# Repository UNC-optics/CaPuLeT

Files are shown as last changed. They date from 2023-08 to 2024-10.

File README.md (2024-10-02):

# An open-source system to integrate Calcium-imaging, Pupillometry, and Locomotion-estimated Tracking (CaPuLeT) in head-fixed mice

Designed by members of the [Pégard](https://www.nicolaspegard.com/) and [Rodríguez-Romaguera](https://www.rodriguezromagueralab.org/) Labs at the University of North Carolina at Chapel Hill, **CaPuLeT** allows researchers to capture locomotion, pupil dynamics, and body kinematics simultaneously. Our system relies on CMOS cameras, an infrared camera placed at eye-level to capture pupil size and an additional camera to record body kinematics. Our system is capable of capturing  locomotion, or the mouse's movement across time, as our wheel system is attached to a mounted rotary encoder. For more information, refer to [Ortiz-Juza et al, 2024](https://star-protocols.cell.com/protocols/3752) [1].



# Graphic User Interface (GUI)

The **CaPuLeT** MATLAB graphical user interface (GUI) allows users to trigger and manage the cameras and LEDs driven by an Arduino microcontroller with a custom shield. Within **CaPuLeT**, users can track locomotion, pupil-size, and *in vivo* calcium imaging data in real-time. 

**Behavioral and Imaging Data Collected**:
- IR Camera → Pupil Dynamics (Dilation and Constriction)
- Additional Camera → Body Kinematics (Body and Tail Movement)
- Rotary Encoder → Locomotion (Speed and Acceleration)
- Multi-Photon Microscope → Neuronal Activity (Intracellular Calcium Concentration)

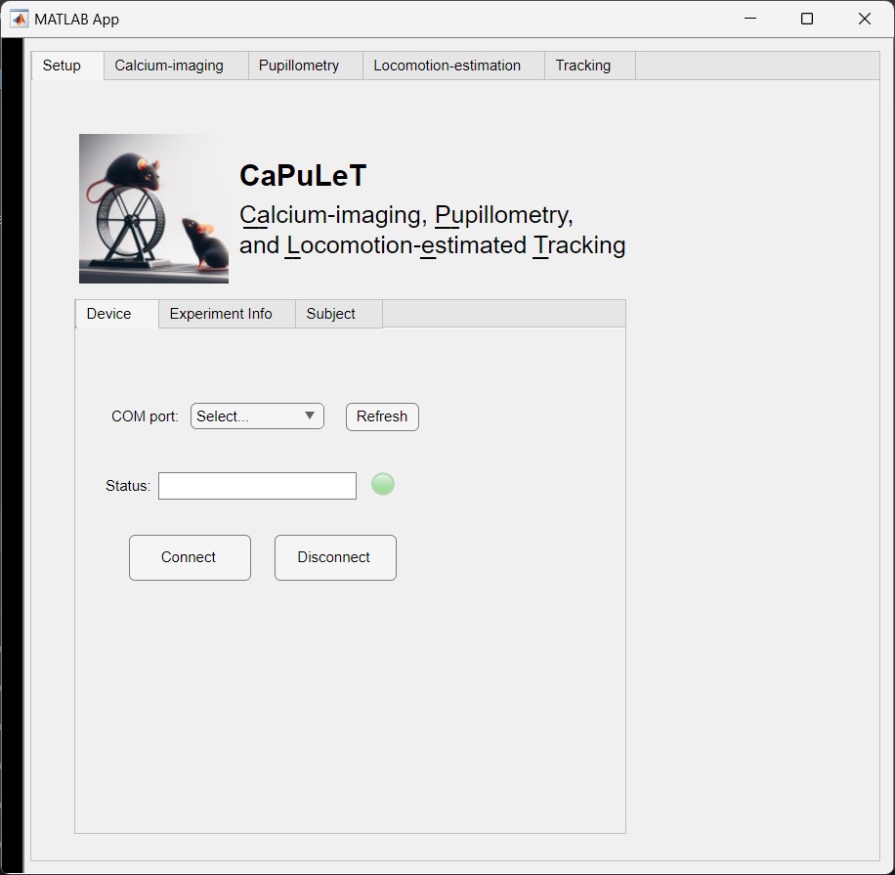
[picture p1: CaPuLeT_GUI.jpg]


# Custom Arduino Printed Circuit Board Shield:
The head-fixation wheel system is driven and controlled by an Arduino Mega 2560 microcontroller board, with a custom printed circuit board (PCB) Arduino shield with built-in resistance, interactive feedback LEDs, real-time clock compatibility, and screw hole terminals. The printed circuit board shield expands the capabilities of the microcontroller board and allows for greater stability than a conventional solderless circuit board. The Arduino shield allows users to interface with each of the components of the **CaPuLeT** GUI. 

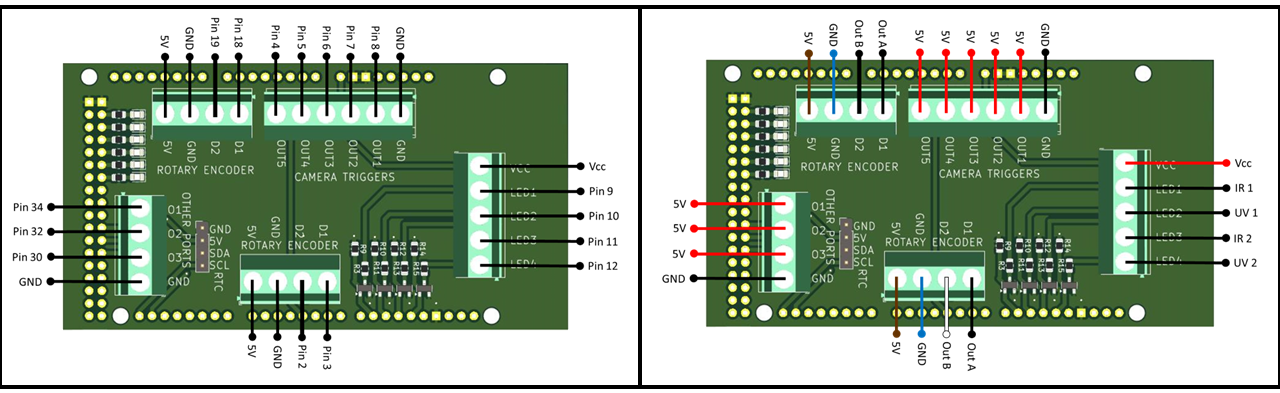
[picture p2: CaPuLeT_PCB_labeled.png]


# Commercially Available and Custom Made Parts 

The following [component list](https://github.com/UNC-optics/CaPuLeT/blob/b9dc13ef048e2fede86db514f3f39af26186ab3a/1-CaPuLeT-Components-Table.pdf) details the manufacturer, part number, and quantity of each item required. This [version](https://github.com/UNC-optics/CaPuLeT/blob/b9dc13ef048e2fede86db514f3f39af26186ab3a/2-CaPuLeT-Color-Coded-Components-Table.pdf) of the component list contains a color coded key which provides an additional layer of support when building the system. 

<table class="table table-bordered table-hover table-condensed">
<thead><tr><th title="Field #1">Part Number</th>
<th title="Field #2">Distributor</th>
<th title="Field #3">Part Name</th>
<th title="Field #4">Distributor Part Number</th>
<th title="Field #5">Quantity Needed</th>
<th title="Field #6">Unit Price</th>
<th title="Field #7">Total Price</th>
</tr></thead>
<tbody><tr>
<td align="right">1</td>
<td>McMaster</td>
<td>5 mm Linear Motion Shaft</td>
<td>6112K37</td>
<td>1</td>
<td>$10.98 </td>
<td>$10.98 </td>
</tr>
<tr>
<td align="right">2</td>
<td>McMaster</td>
<td>Clear Impact-Resistant Polycarbonate Film</td>
<td>85585K15</td>
<td>1</td>
<td>$8.35 </td>
<td>$8.35 </td>
</tr>
<tr>
<td align="right">3</td>
<td>McMaster</td>
<td>Female Threaded Round Standoff</td>
<td>93330A541</td>
<td>10</td>
<td>$2.13 </td>
<td>$21.30 </td>
</tr>
<tr>
<td align="right">4</td>
<td>McMaster</td>
<td>Socket Head Screw M3 x 0.5 mm Thread, 6 mm Long</td>
<td>91290A111</td>
<td>1 (Pack of 100)</td>
<td>$10.91 </td>
<td>$10.91 </td>
</tr>
<tr>
<td align="right">5</td>
<td>Polulu</td>
<td>Aluminum Mounting Hub for 5mm Shaft</td>
<td>1203</td>
<td>1 (Pack of 2)</td>
<td>$18.90 </td>
<td>$18.90 </td>
</tr>
<tr>
<td align="right">6</td>
<td>Polulu</td>
<td>Machine Screw: #4-40, 1/2? Length, Phillips</td>
<td>1962</td>
<td>1 (Pack of 25)</td>
<td>$1.39 </td>
<td>$1.39 </td>
</tr>
<tr>
<td align="right">7</td>
<td>Thorlabs</td>
<td>0.75 Inch Post</td>
<td>TR075</td>
<td>1</td>
<td>$5.38 </td>
<td>$5.38 </td>
</tr>
<tr>
<td align="right">8</td>
<td>Thorlabs</td>
<td>2 Inch Post</td>
<td>TR2</td>
<td>2</td>
<td>$5.90 </td>
<td>$11.80 </td>
</tr>
<tr>
<td align="right">9</td>
<td>Thorlabs</td>
<td>3 Inch Post</td>
<td>TR3</td>
<td>2</td>
<td>$6.15 </td>
<td>$12.30 </td>
</tr>
<tr>
<td align="right">10</td>
<td>Thorlabs</td>
<td>4 Inch Post, 5 Pack</td>
<td>TR4-P5</td>
<td>1 (Pack of 5)</td>
<td>$30.00 </td>
<td>$30.00 </td>
</tr>
<tr>
<td align="right">11</td>
<td>Thorlabs</td>
<td>6 Inch Post</td>
<td>TR6</td>
<td>2</td>
<td>$8.09 </td>
<td>$16.18 </td>
</tr>
<tr>
<td align="right">12</td>
<td>Thorlabs</td>
<td>8 Inch Post</td>
<td>TR8</td>
<td>2</td>
<td>$9.69 </td>
<td>$19.38 </td>
</tr>
<tr>
<td align="right">13</td>
<td>Thorlabs</td>
<td>10 Inch Post</td>
<td>TR10</td>
<td>2</td>
<td>$10.76 </td>
<td>$21.52 </td>
</tr>
<tr>
<td align="right">14</td>
<td>Thorlabs</td>
<td>2 Inch Post Holder</td>
<td>PH2</td>
<td>1</td>
<td>$8.95 </td>
<td>$8.95 </td>
</tr>
<tr>
<td align="right">15</td>
<td>Thorlabs</td>
<td>3 Inch Post Holder</td>
<td>PH3</td>
<td>4</td>
<td>$9.62 </td>
<td>$38.48 </td>
</tr>
<tr>
<td align="right">16</td>
<td>Thorlabs</td>
<td>6 Inch Post Holder</td>
<td>PH6</td>
<td>1</td>
<td>$14.70 </td>
<td>$14.70 </td>
</tr>
<tr>
<td align="right">17</td>
<td>Thorlabs</td>
<td>Right Angle End Clamp</td>
<td>RA180</td>
<td>4</td>
<td>$12.34 </td>
<td>$49.36 </td>
</tr>
<tr>
<td align="right">18</td>
<td>Thorlabs</td>
<td>Rotating Clamp</td>
<td>SWC</td>
<td>1</td>
<td>$26.91 </td>
<td>$26.91 </td>
</tr>
<tr>
<td align="right">19</td>
<td>Thorlabs</td>
<td>Right Angle Post Clamp</td>
<td>RA90TR</td>
<td>1</td>
<td>$17.82 </td>
<td>$17.82 </td>
</tr>
<tr>
<td align="right">20</td>
<td>Thorlabs</td>
<td>Mini Optical Post</td>
<td>MS3R</td>
<td>1</td>
<td>$9.09 </td>
<td>$9.09 </td>
</tr>
<tr>
<td align="right">21</td>
<td>Thorlabs</td>
<td>Aluminum Breadboard 8&quot; x 10&quot; x 1/2&quot;, 1/4&quot;-20 Taps</td>
<td>MB810</td>
<td>1</td>
<td>$131.60 </td>
<td>$131.60 </td>
</tr>
<tr>
<td align="right">22</td>
<td>Thorlabs</td>
<td>Aluminum Breadboard 12&quot; x 18&quot; x 1/2&quot;, 1/4&quot;-20 Taps</td>
<td>MB1218</td>
<td>1</td>
<td>$214.65 </td>
<td>$214.65 </td>
</tr>
<tr>
<td align="right">23</td>
<td>Thorlabs</td>
<td>Breadboard Lifting Handles, Reinforced Polymer </td>
<td>BBH1</td>
<td>2 (Pack of 2)</td>
<td>$17.01 </td>
<td>$17.01 </td>
</tr>
<tr>
<td align="right">24</td>
<td>Thorlabs</td>
<td>4-40 Stainless Steel Cap Screw, 3/8&quot; Long</td>
<td>SH4S038</td>
<td>1 (Pack of 50)</td>
<td>$9.31 </td>
<td>$9.31 </td>
</tr>
<tr>
<td align="right">25</td>
<td>Thorlabs</td>
<td>Spring-Loaded 3/16&quot; Hex-Locking Thumbscrew, 1/4&quot;-20 Thread</td>
<td>TS25H</td>
<td>2</td>
<td>$2.87 </td>
<td>$5.74 </td>
</tr>
<tr>
<td align="right">26</td>
<td>Thorlabs</td>
<td>1/4&quot;-20 Stainless Steel Setscrew, 5/8&quot; Long (Adaptor)</td>
<td>SS25S0625</td>
<td>1 (Pack of 25)</td>
<td>$6.97 </td>
<td>$6.97 </td>
</tr>
<tr>
<td align="right">27</td>
<td>Thorlabs</td>
<td>1/4&quot; Washer, M6 Compatible, Stainless Steel</td>
<td>W25S050</td>
<td>1 (Pack of 100)</td>
<td>$10.20 </td>
<td>$10.20 </td>
</tr>
<tr>
<td align="right">28</td>
<td>Thorlabs</td>
<td>1/4&quot;-20 Stainless Steel Nut</td>
<td>N25S0440</td>
<td>1 (Pack of 50)</td>
<td>$6.43 </td>
<td>$6.43 </td>
</tr>
<tr>
<td align="right">29</td>
<td>Omron</td>
<td>Rotary Encoder - 1024 P/R (Quadrature)</td>
<td>E6B2-CWZ3E (E69-C06B)</td>
<td>1</td>
<td>$48.50 </td>
<td>$48.50 </td>
</tr>
<tr>
<td align="right">30</td>
<td>DB Unlimited</td>
<td>Speaker 80hm 5 w top port 104db</td>
<td>2104-SP500208-3-ND</td>
<td>1</td>
<td>$6.79 </td>
<td>$6.79 </td>
</tr>
<tr>
<td align="right">31</td>
<td>SullinsCorp</td>
<td>2.54mm Pitch Single Row Pin Header Strip</td>
<td>PREC040SAAN-RC</td>
<td>3</td>
<td>$1.53</td>
<td>$1.53</td>
</tr>
<tr>
<td align="right">32</td>
<td>Ardest</td>
<td>2N2222 NPN TO-92 Power Transistors</td>
<td>2N2222</td>
<td>6</td>
<td>$1.44</td>
<td>$1.44</td>
</tr>
<tr>
<td align="right">33</td>
<td>Boca Bearings</td>
<td>5 mm Steel Ball Bearing</td>
<td>SMR115-ZZC #5 LD</td>
<td>2</td>
<td>$10.58 </td>
<td>$21.16 </td>
</tr>
<tr>
<td align="right">34</td>
<td>Xenocam</td>
<td>9-22mm 1/3" F1.4 M12-mount lens with IR filter</td>
<td>XC0922LENS</td>
<td>1</td>
<td>$19.99 </td>
<td>$19.99 </td>
</tr>
<tr>
<td align="right">35</td>
<td>Monoprice</td>
<td>USB 2.0 Type-A Male to Mini-B 5pin Male Cable (Monoprice)</td>
<td>B002KL8J8W</td>
<td>1</td>
<td>$4.78</td>
<td>$4.78</td>
</tr>
<tr>
<td align="right">36</td>
<td>Computar</td>
<td>0.33-Inch Varifocal lens 2.8-12mm F1.3 Auto Iris (Computar)</td>
<td>B002HRE2ZS / TG4Z2813FCS-IR</td>
<td>1(Used)</td>
<td>$19.99 </td>
<td>$19.99 </td>
</tr>
<tr>
<td align="right">37</td>
<td>Chanzon</td>
<td>3 mm UV light, 395-400nm (Chanzon)</td>
<td>100F3T-YT-WH-PU</td>
<td>1 (Pack of 100)</td>
<td>$6.99 </td>
<td>$6.99 </td>
</tr>
<tr>
<td align="right">38</td>
<td>Adafruit</td>
<td>5 mm super-bright IR LED, 940nm (Adafruit)</td>
<td>ADA388 / B00ULB0U44</td>
<td>1 (Pack of 25)</td>
<td>$10.98 </td>
<td>$10.98 </td>
</tr>
<tr>
<td align="right">39</td>
<td>Fermerry</td>
<td>24 AWG 50 feet Electrical Wire (Fermerry)</td>
<td>B089CX3FVV</td>
<td>1</td>
<td>$26.99 </td>
<td>$26.99 </td>
</tr>
<tr>
<td align="right">40</td>
<td>Arduino</td>
<td>Arduino Mega 2560 Rev3 Microcontroller Board (Arduino)</td>
<td>A000067 / B0046AMGW0</td>
<td>1</td>
<td>$48.99 </td>
<td>$48.99 </td>
</tr>
<tr>
<td align="right">41</td>
<td>Arduino</td>
<td>USB 2.0 Cable Type A/B (Arduino)</td>
<td>M000006 / B013EOQUAW</td>
<td>1</td>
<td>$7.00 </td>
<td>$7.00 </td>
</tr>
<tr>
<td align="right">42</td>
<td>Tnisesm</td>
<td>PCB Mount Screw Terminal Block Connectors (Tnisesm)</td>
<td>CATN-T03B</td>
<td>1</td>
<td>$8.99 </td>
<td>$8.99 </td>
</tr>
<tr>
<td align="right">43</td>
<td>Adeep</td>
<td>Real Time Clock Module DS3231 AT24C32 IIC (Adeept)</td>
<td>2pcsDS3231 / B097PMNMQZ</td>
<td>1 (Pack of 2)</td>
<td>$7.99 </td>
<td>$7.99 </td>
</tr>
<tr>
<td align="right">44</td>
<td>LiCB</td>
<td>3V Lithium Battery (Junpower)</td>
<td>CR2032 / B07LGL9LQ1</td>
<td>1 (Pack of 10)</td>
<td>$4.99 </td>
<td>$4.99 </td>
</tr>
<tr>
<td align="right">45</td>
<td>ELECFUN</td>
<td>Heat Shrink Tubing (Electfun)</td>
<td>RSG-KIT350</td>
<td>1</td>
<td>$14.99 </td>
<td>$14.99 </td>
</tr>
<tr>
<td align="right">46</td>
<td>Yancorp</td>
<td>Black Adhesive contact paper (Yancorp)</td>
<td>B082CPSVPW</td>
<td>1</td>
<td>$6.98 </td>
<td>$6.98 </td>
</tr>
<tr>
<td align="right">47</td>
<td>Weld-On</td>
<td>IPS Weld-On 3 Acrylic Plastic Cement (Weld-On)</td>
<td>?TLLPN-21847771</td>
<td>1</td>
<td>$28.55 </td>
<td>$28.55 </td>
</tr>
<tr>
<td align="right">48</td>
<td>CENTROPOWER</td>
<td>12V 5A DC Power Cable Male Female Connector (Centro Power)</td>
<td>DCCORD-MF</td>
<td>1 (Pack of 10)</td>
<td>$9.19 </td>
<td>$9.19 </td>
</tr>
<tr>
<td align="right">49</td>
<td>CENTROPOWER</td>
<td>12V DC Power Connector Barrel Adaptor (Centro Power)</td>
<td>B07C61434H</td>
<td>1 (Pack of 10)</td>
<td>$7.99 </td>
<td>$7.99 </td>
</tr>
<tr>
<td align="right">50</td>
<td>ALITOVE</td>
<td>12V Red LED Flexible Strip Ribbon Light (Alitrove, 16.4 feet)</td>
<td>AL5RWPBK12V</td>
<td>1</td>
<td>$13.99 </td>
<td>$13.99 </td>
</tr>
<tr>
<td align="right">51</td>
<td>Mifasopower</td>
<td>Power Strip Surge Protector 10Ft (Mifaso Power)</td>
<td>MFS311T</td>
<td>1</td>
<td>$19.99 </td>
<td>$19.99 </td>
</tr>
<tr>
<td align="right">52</td>
<td>Sumato Stuff</td>
<td>Anti Vibration Pads (Functional Necessities)</td>
<td>SSHI00003</td>
<td>1 (Pack of 4)</td>
<td>$14.99 </td>
<td>$14.99 </td>
</tr>
<tr>
<td align="right">53</td>
<td>Focusound</td>
<td>1&quot; x 12&quot; x 12&quot; Sound Absorption Wall Panels (Xin &amp; Log)</td>
<td>FS0302A</td>
<td>1 (Pack of 24)</td>
<td>$17.99 </td>
<td>$17.99 </td>
</tr>
<tr>
<td align="right">54</td>
<td>TANTTI</td>
<td>4 inch Zip Ties with 18 lb Tensile Strength</td>
<td>604477847283</td>
<td>1 (Pack of 200)</td>
<td>$3.99 </td>
<td>$3.99 </td>
</tr>
<tr>
<td align="right">55</td>
<td>3M</td>
<td>3M Scotch Super 33+ Electrical Tape - 3/4 in x 52 ft</td>
<td>MMM06133</td>
<td>1</td>
<td>$4.98 </td>
<td>$4.98 </td>
</tr>
<tr>
<td align="right">56</td>
<td>Amazon</td>
<td>Hirose 4 Pin Female HR10A-7P-4S to Flying Leads Power Cable (Alvin’s Cables)</td>
<td>HR10A-7P-4S(73)</td>
<td>1</td>
<td>$25.99 </td>
<td>$25.99</td>
</tr>
<tr>
<td align="right">57</td>
<td>Custom Machined Parts</td>
<td>Rotary Encoder Adaptor (Aluminum 304)</td>
<td>CNC Machining (eMachineShop)</td>
<td>6 (Bulk Purchase)</td>
<td>$28.43 </td>
<td>$170.62 </td>
</tr>
<tr>
<td align="right">58</td>
<td>Custom Machined Parts</td>
<td>Head Plate Holder (Aluminum 304)</td>
<td>CNC Machining (eMachineShop)</td>
<td>12 (Bulk Purchase)</td>
<td>$30.20 </td>
<td>$362.44 </td>
</tr>
<tr>
<td align="right">59</td>
<td>Custom Machined Parts</td>
<td>Head Plate (Top Piece) (Aluminum 304)</td>
<td>CNC Machining (eMachineShop)</td>
<td>6 (Bulk Purchase)</td>
<td>$39.14 </td>
<td>$234.85 </td>
</tr>
<tr>
<td align="right">60</td>
<td>Custom Machined Parts</td>
<td>Head Plate (Bottom Piece) (Aluminum 304)</td>
<td>CNC Machining (eMachineShop)</td>
<td>6 (Bulk Purchase)</td>
<td>$51.01 </td>
<td>$306.04 </td>
</tr>
<tr>
<td align="right">61</td>
<td>Custom Machined Parts</td>
<td>Head rings (Aluminum 6061-T6)</td>
<td>CNC Machining (eMachineShop)</td>
<td>100 (Bulk Purchase)</td>
<td>$5.16 </td>
<td>$258.22 </td>
</tr>
<tr>
<td align="right">62</td>
<td>Custom Machined Parts</td>
<td>Rotary Wheel (1/8 Thick Clear Cast Acrylic)</td>
<td>Laser Cutting (Ponoko)</td>
<td>2</td>
<td>$61.06 </td>
<td>$61.06 </td>
</tr>
<tr>
<td align="right">63</td>
<td>Custom Machined Parts</td>
<td>Rotary Wheel Curved Surface (Clear Cast Acrylic)</td>
<td>Laser Cutting / Manual Cutting</td>
<td>1</td>
<td>$0.00 </td>
<td>$0.00 </td>
</tr>
<tr>
<td align="right">64</td>
<td>Custom Machined Parts</td>
<td>Rotary Wheel Curved Surface (Black Adhesive Contact Paper)</td>
<td>Laser Cutting / Manual Cutting</td>
<td>1</td>
<td>$0.00 </td>
<td>$0.00 </td>
</tr>
<tr>
<td align="right">65</td>
<td>Custom Machined Parts</td>
<td>Waste Management Ramp (Resin)</td>
<td>3-D Printing (Craftcloud3d)</td>
<td>1</td>
<td>$57.76 </td>
<td>$57.76 </td>
</tr>
<tr>
<td align="right">66</td>
<td>Custom Machined Parts</td>
<td>Arduino Mega 2560 Rev3 Protective Case (Resin)</td>
<td>3-D Printing (Craftcloud3d)</td>
<td>1</td>
<td>$16.06 </td>
<td>$16.06 </td>
</tr>
<tr>
<td align="right">67</td>
<td>Custom Machined Parts</td>
<td>Arduino Mega 2560 Rev3 Shield SMT PCB</td>
<td>PCB Manufacturing (JLC PCB)</td>
<td>1</td>
<td>X</td>
<td>X</td>
</tr>
<tr>
<td align="right">68</td>
<td>FLIR</td>
<td>Firefly S Camera</td>
<td>FFY-U3-16S2M-S</td>
<td>1</td>
<td>$234.00 </td>
<td>$234.00 </td>
</tr>
<tr>
<td align="right">69</td>
<td>FLIR</td>
<td>Tripod Adapter for Firefly S Camera</td>
<td>ACC-01-0017</td>
<td>1</td>
<td>$32.10 </td>
<td>$32.10 </td>
</tr>
<tr>
<td align="right">70</td>
<td>FLIR</td>
<td>USB 3.1 Locking Cable</td>
<td>ACC-01-2300</td>
<td>1</td>
<td>$24.60 </td>
<td>$24.60 </td>
</tr>
<tr>
<td align="right">71</td>
<td>FLIR</td>
<td>GPIO cable w/ 6 pins</td>
<td>ACC-01-3015</td>
<td>1</td>
<td>$9.60 </td>
<td>$9.60 </td>
</tr>
<tr>
<td align="right">72</td>
<td>The Imaging Source</td>
<td>USB 2.0 CMOS Monochrome Camera</td>
<td>DMK-22BUC03</td>
<td>1</td>
<td>$234.00 </td>
<td>$234.00 </td>
</tr>
<tr>
<td align="right">73</td>
<td>SYSRACKS</td>
<td>15U 35&quot; Depth Under Desk Sound Proof Server Cabinet</td>
<td>SP15.900</td>
<td>1</td>
<td>$1,122.00 </td>
<td>$1,122.00 </td>
</tr>
</tbody></table>

This [document](https://github.com/UNC-optics/CaPuLeT/blob/b9dc13ef048e2fede86db514f3f39af26186ab3a/4-CaPuLeT-Custom-Parts-Table.pdf) outlines the design of each of the custom pieces and the file types found within this repository that can be used to replicate the system. More details regarding the specifications of the custom parts can be found [here](https://github.com/UNC-optics/CaPuLeT/blob/b9dc13ef048e2fede86db514f3f39af26186ab3a/5-CaPuLeT-Custom-Parts-Specifications.pdf). The following [spreadsheet](https://github.com/UNC-optics/CaPuLeT/blob/b9dc13ef048e2fede86db514f3f39af26186ab3a/3-CaPuLeT-Cost-Spreadsheet.xlsx) outlines the total cost of the system.  




**Here is a list of the manufacturers we purchased materials from:** 
- McMaster-Carr
- Pololu
- Thorlabs
- SparkFun
- Digikey
- Amazon
- FLIR
- The Imaging Source
- SYSRACKS

**Here is a list of companies you can purchase custom parts from, if not fabricated in-house:**
- eMachineShop (CNC Machining)
- Ponoko (Laser Cutting)
- Craftcloud3d (3-D Printing)
- JBL PCB (PCB Printing / Soldering)

# Step-by-Step Building Guide

**A fully functioning system requires users to build the following elements from the materials purchased:**
- Locomotion Wheel
- Headplate Fixation System
- IR / UV LEDs

**Additionally, the following commercial materials need to modified to be used within our system:**
- Rotary Encoder
- GPIO Cable
- Hirose Cable
- Overhead Speaker
- Ambient Noise Fan
- Red LED Strips

This following [guide](https://github.com/UNC-optics/CaPuLeT/blob/b9dc13ef048e2fede86db514f3f39af26186ab3a/6-CaPuLeT-Step-by-Step-Guide.pdf) provides a step-by-step walkthrough for building and modifying each of the required components. This document includes diagrams and explanations for assembling each of the final components of the build. 

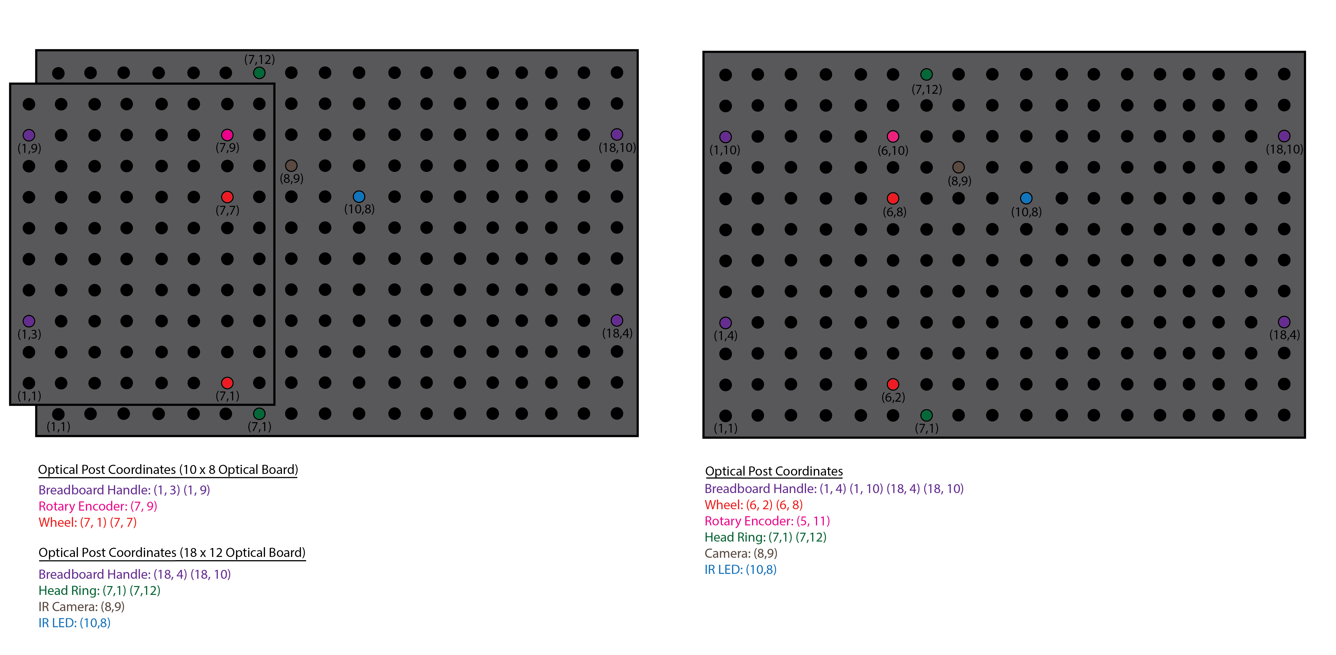
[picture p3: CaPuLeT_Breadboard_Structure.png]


# Software Installation Guide and Dependencies

Following this installation guide will ensure that your system will be able to run the set of MATLAB scripts and Arduino IDE sketches we have provided. Our system is run primarily on MATLAB's interface. While other software is used to first initialize components, such as Arduino IDE for the rotary encoder and Spinnaker SDK for the cameras, the subsequent input signals and data acquisition steps are performed exclusively with MATLAB. 

**Required Software and Applications**:
- [MATLAB R2022a](https://www.mathworks.com/products/new_products/release2022a.html)
- [Arduino IDE](https://www.arduino.cc/en/software)
- [Spinnaker SDK](https://www.flir.com/products/spinnaker-sdk/)
- [DeepLabCuts](https://github.com/DeepLabCut/DeepLabCut)
  
Our MATLAB scripts are based on MATLAB R2022a, a previous version of the software application. Running our scripts on a more recent version of the application will result in a number of errors. After downloading MATLAB R2022a, you will need to download a number of toolboxes and add-ons. 

**Base Toolboxes**:
- Data Acquisition Toolbox
- Image Acquisition Toolbox
- Image Processing Toolbox
- Statistics and Machine Learning Toolbox 

**Additional Toolbox Support Packages**:
- Data Acquisition Toolbox Support Package for National Instruments NI-DAQmx Devices
- Image Acquisition Toolbox Support Package for GenICam Interface
- Image Acquisition Toolbox Support Package OS Generic Video Interface
- Image Acquisition Toolbox Support Package for Point Grey Hardware
- Image Acquisition Toolbox Support Support Package for GigE Vision Hardware
- MATLAB Support Package for Arduino Hardware

Finally, users will need to download the following drivers to generate a connection between their computer system and an external hardware device. In our case, we need to download two drivers to interface with the additional camera used in our system.

**Driver Requirements**:
- USB3 Driver
- [DMK 22BUC03 Driver](https://www.oemcameras.com/dmk-22buc03.htm)
- [Spinnaker SDK USB3 Vision Cameras Driver](https://www.flir.com/products/spinnaker-sdk/)
- [IC Matlab Plugin for Matlab (Version 3.4.0.58)](https://www.theimagingsource.com/en-us/support/download/icmatlabr2013b-3.4.0.58/)

**Library Requirements**:
- [DS3231 Library](https://github.com/NorthernWidget/DS3231)
  
# Contact

Further information and requests for resources should be directed to and will be fulfilled by the lead contact and corresponding author, Jose Rodriguez-Romaguera (jose_rodriguezromaguera@med.unc.edu). Example pupillometric and locomotion data is available upon request to the technical contact and corresponding author, Nicolas C. Pégard (pegard@unc.edu).

# Citation 

If you replicate this system in your own labs or use parts of our designs and code, we kindly ask that you please cite [Ortiz-Juza et al, 2024](https://star-protocols.cell.com/protocols/3752) [1]. 

[1] Ortiz-Juza, M. M., Tormes-Vaquerano, J., Hegel, S. M., Curtis, V. R., Alghorazi, R. A., Miller, N. W., McTaggart, E. M., Pégard, N. C., & Rodriguez-Romaguera, J. (2024). Protocol for an open-source system to integrate calcium imaging, pupillometry, and locomotion-estimated tracking in head-fixed mice. STAR Protocols, 5(4), 103331. https://doi.org/10.1016/j.xpro.2024.103331

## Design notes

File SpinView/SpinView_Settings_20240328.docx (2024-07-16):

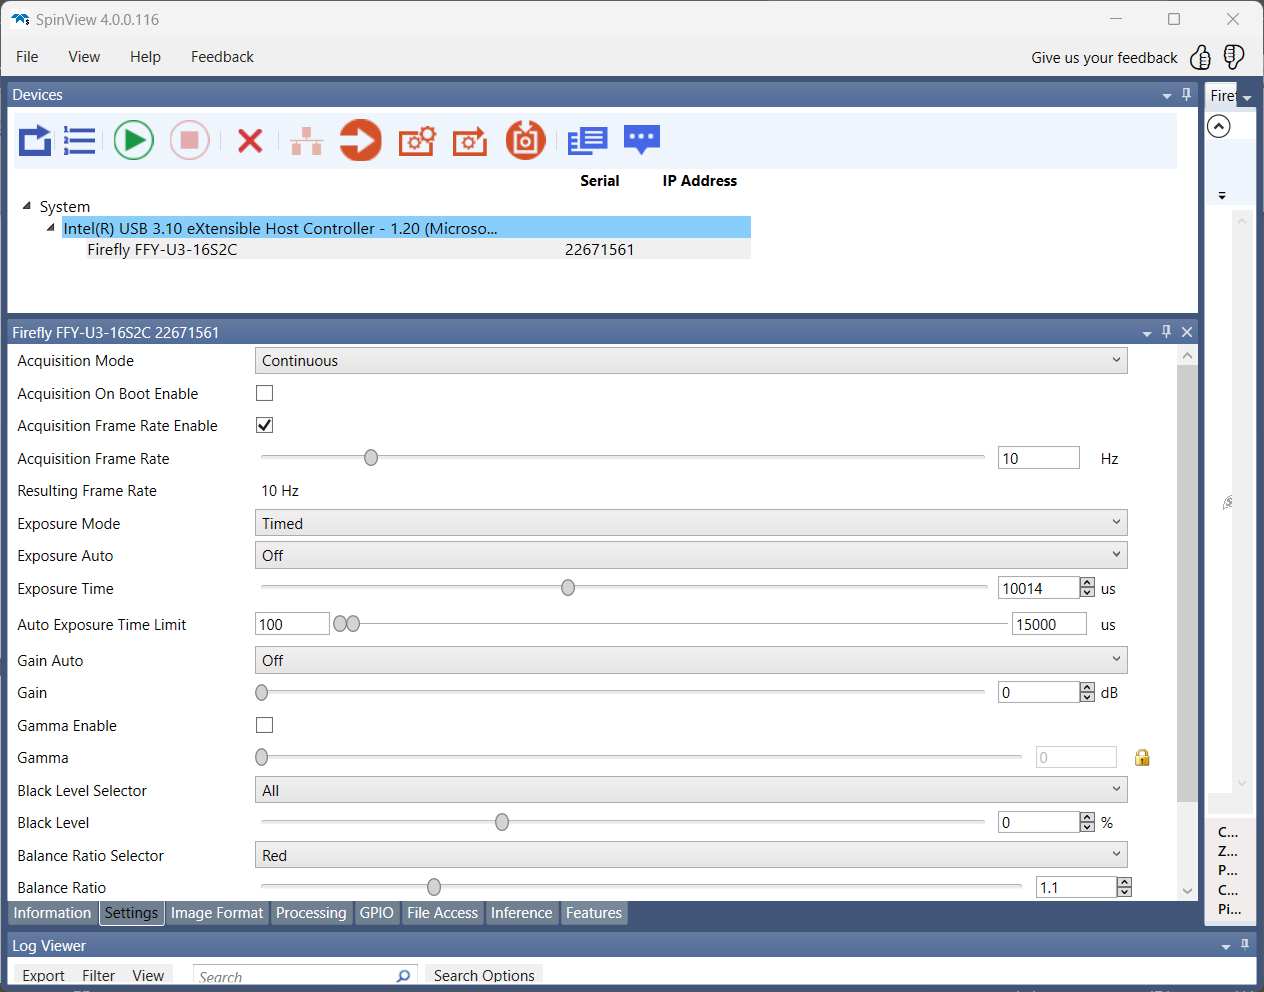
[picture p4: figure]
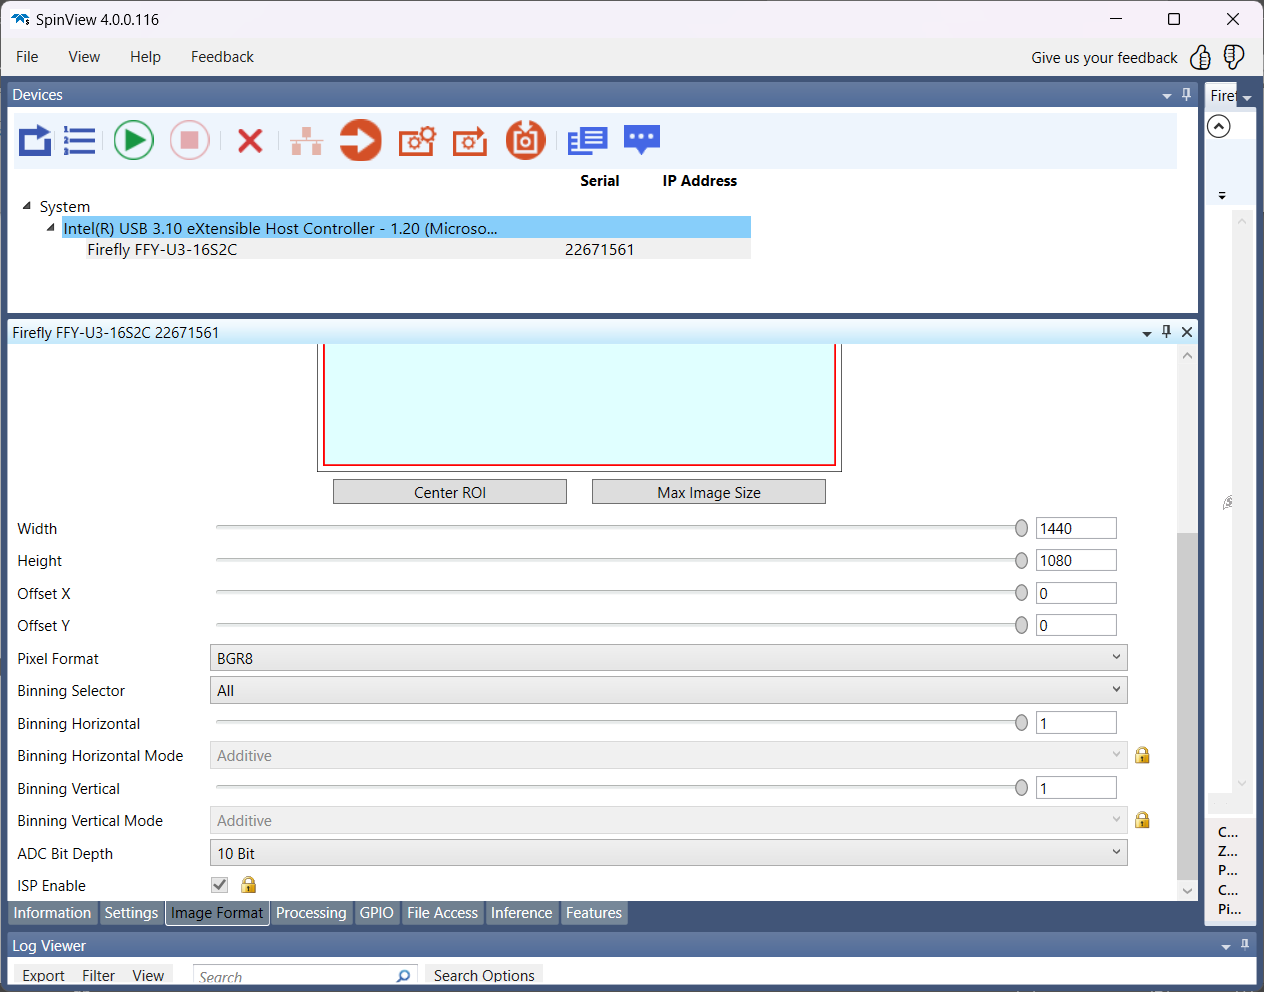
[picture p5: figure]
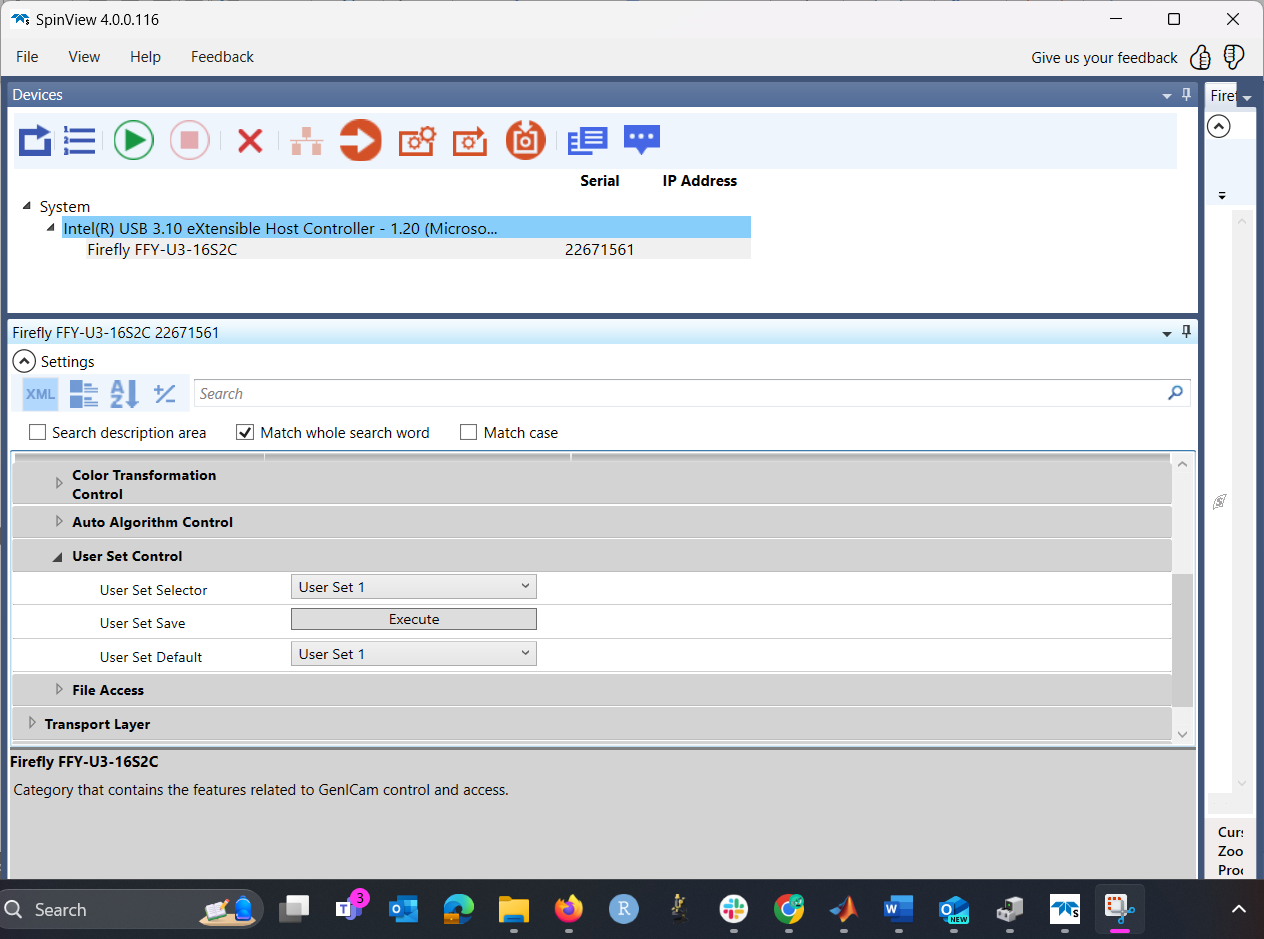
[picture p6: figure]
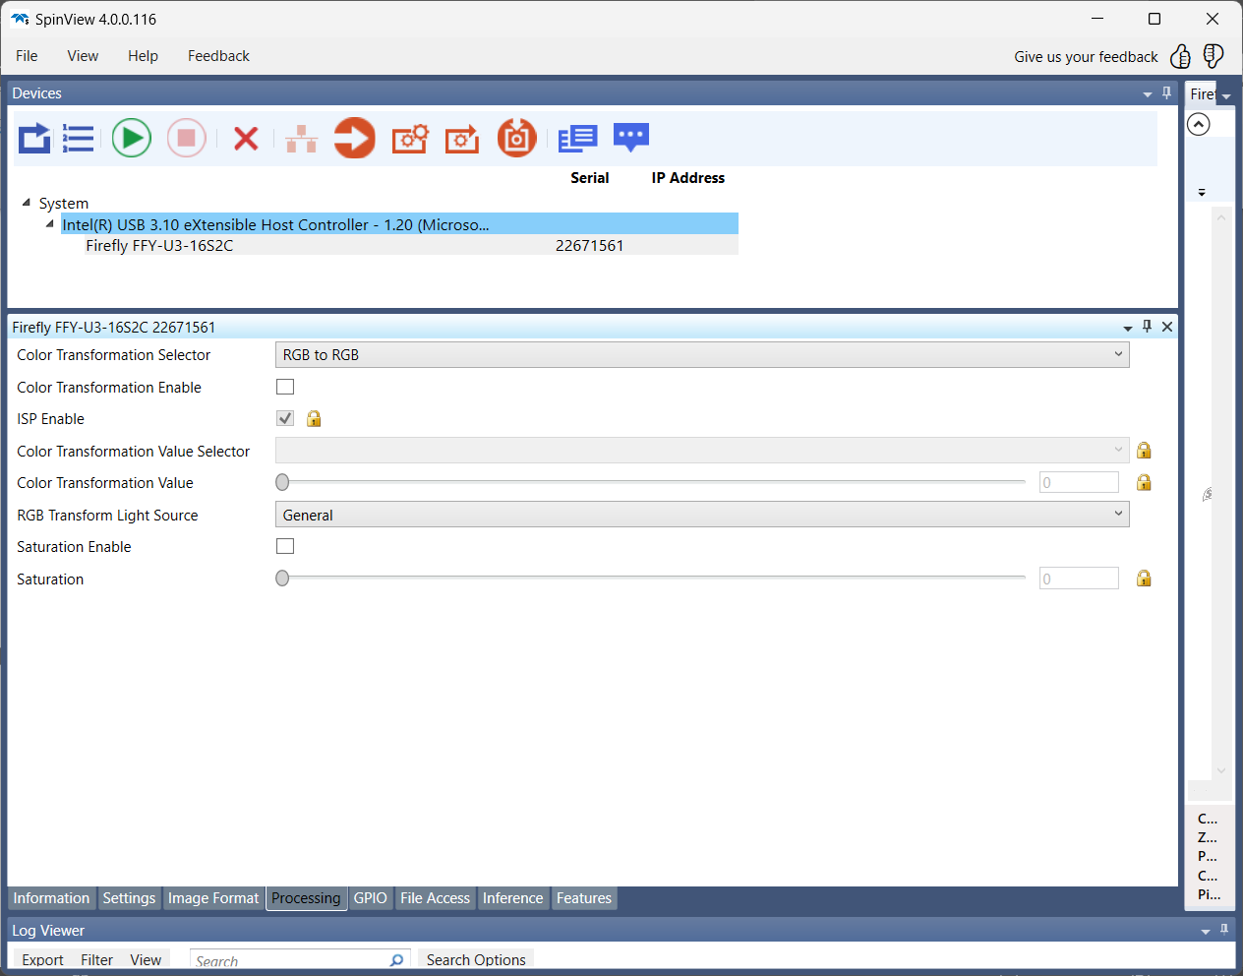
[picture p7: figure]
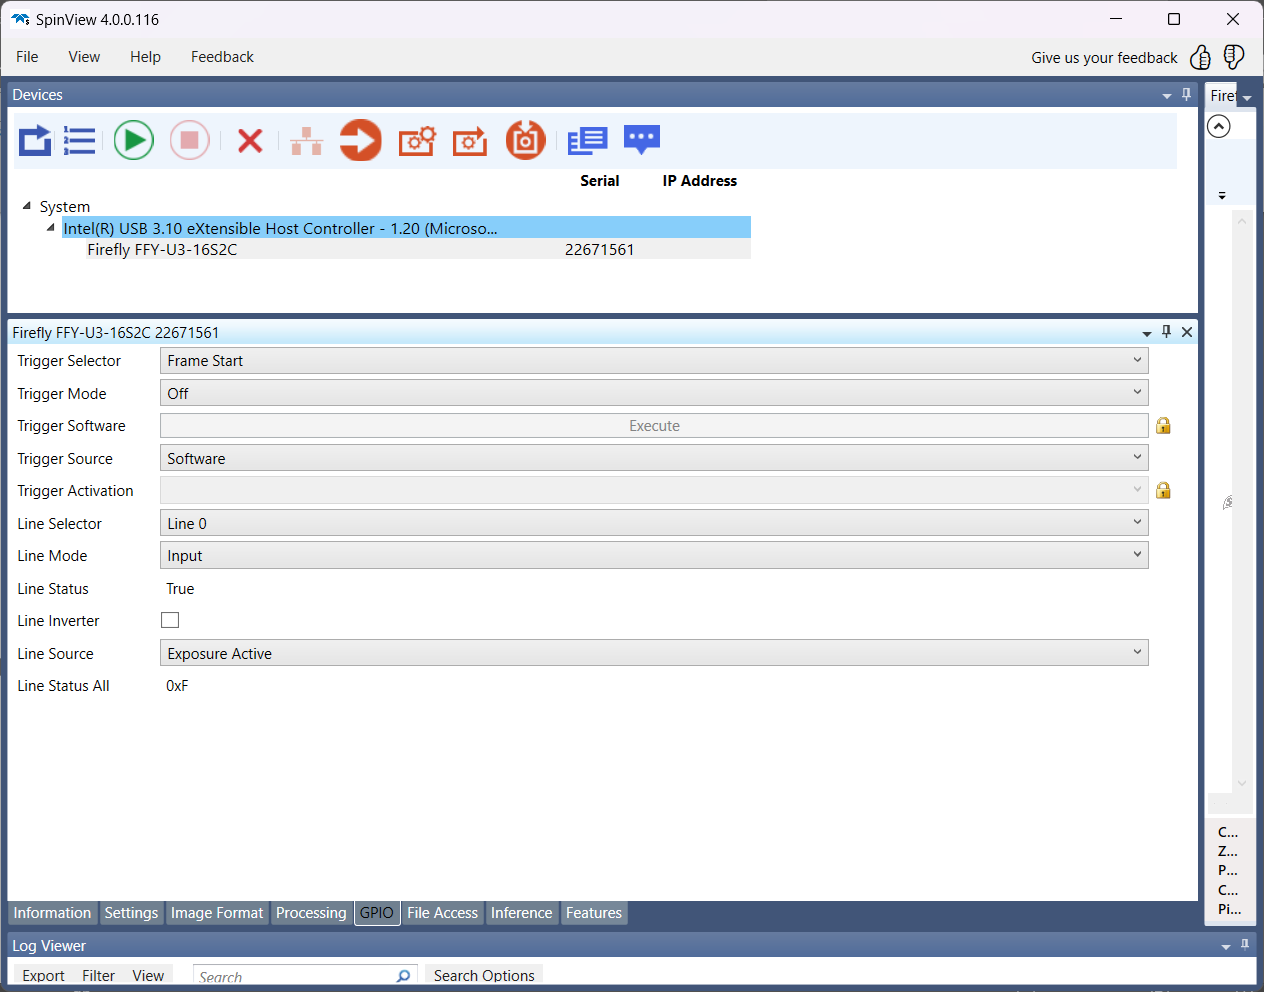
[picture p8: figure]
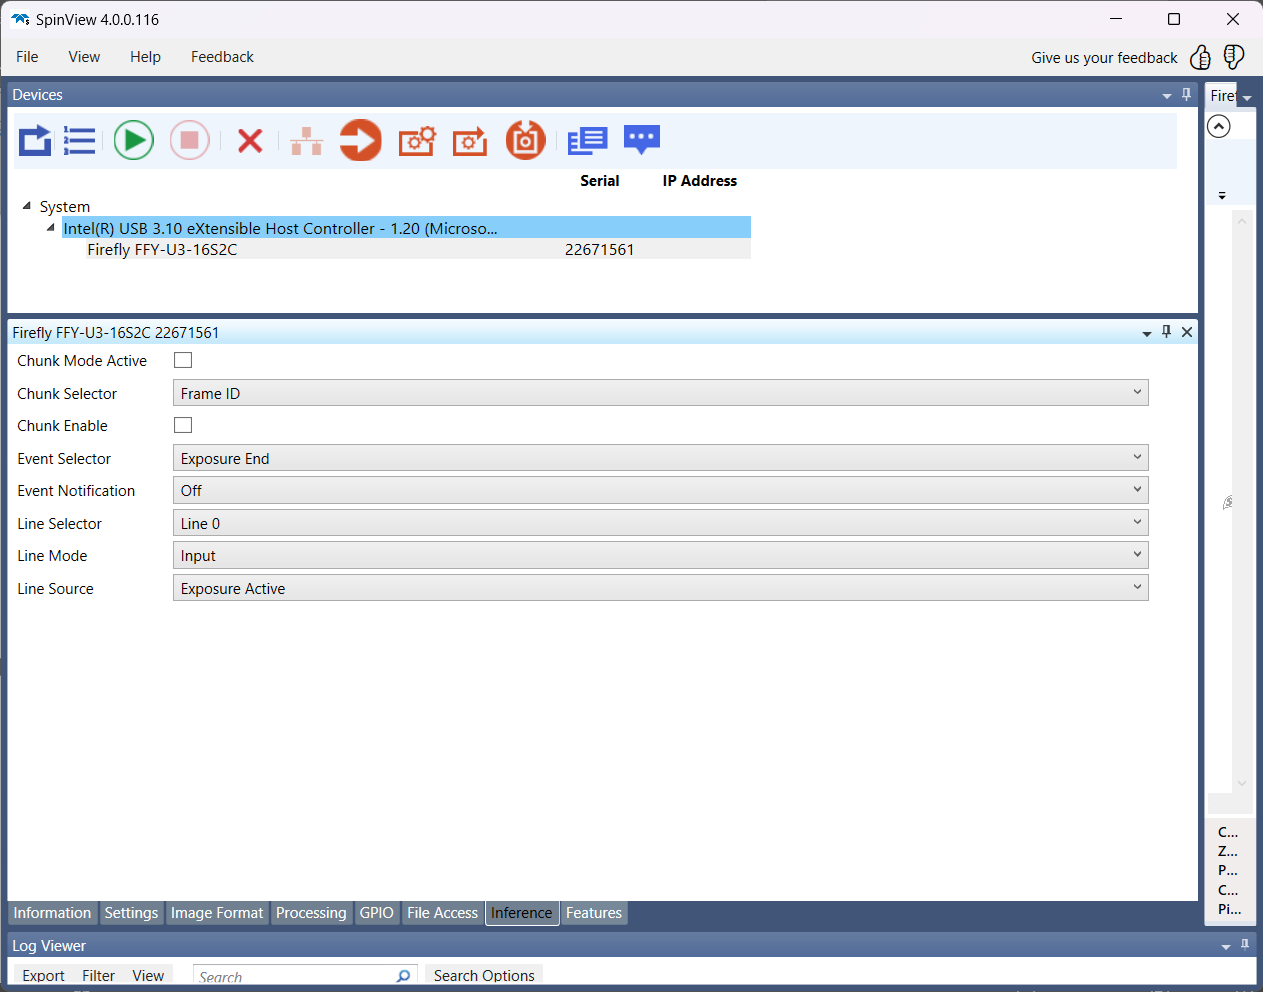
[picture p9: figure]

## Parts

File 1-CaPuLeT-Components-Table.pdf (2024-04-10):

Part Name | Part / Identification Number | Quantity

McMaster-Carr

5 mm Linear Motion Shaft | 6112K37 | 1
Clear Impact-Resistant Polycarbonate Film | 85585K15 | 1
Female Threaded Round Standoff | 93330A541 | 10
Socket Head Screw M3 x 0.5 mm Thread, 6 mm Long | 91290A111 | 1 (Pack of 100)

Pololu

Aluminum Mounting Hub for 5mm Shaft | 1203 | 1 (Pack of 2)
Machine Screw: #4-40, 1/2″ Length, Phillips | 1962 | 1 (Pack of 25)

Thorlabs

0.75 Inch Post | TR075 | 1
2 Inch Post | TR2 | 2
3 Inch Post | TR3 | 2
4 Inch Post | TR4 | 5
6 Inch Post | TR6 | 2
8 Inch Post | TR8 | 2
10 Inch Post | TR10 | 2
2 Inch Post Holder | PH2 | 1
3 Inch Post Holder | PH3 | 4
6 Inch Post Holder | PH6 | 1
Right Angle End Clamp | RA180 | 4
Rotating Clamp | SWC | 1
Right Angle Post Clamp | RA90TR | 1
Mini Optical Post | MS3R | 1
Aluminum Breadboard 8" x 10" x 1/2", 1/4"-20 Taps | MB810 | 1
Aluminum Breadboard 12" x 18" x 1/2", 1/4"-20 Taps | MB1218 | 1

Breadboard Lifting Handles, Reinforced Polymer | BBH1 | 1 (Pack of 2)
4-40 Stainless Steel Cap Screw, 3/8" Long | SH4S038 | 1 (Pack of 50)
Spring-Loaded 3/16" Hex-Locking Thumbscrew, 1/4"-20 Thread | TS25H | 2
1/4"-20 Stainless Steel Setscrew, 5/8" Long (Adaptor) | SS25S0625 | 1 (Pack of 25)
1/4" Washer, M6 Compatible, Stainless Steel | W25S050 | 1 (Pack of 100)
1/4"-20 Stainless Steel Nut | N25S0440 | 1 (Pack of 50)

SparkFun

Rotary Encoder (Resin Coupling Adaptor Included) | E6B2-CWZ3E (E69-C06B) | 1

Digikey

Speaker 80hm 5w top port 104db | 2104-SP500208-3-ND | 1
2.54mm Pitch Single Row Pin Header Strip | S1012EC-40-ND | 1
2N2222 NPN TO-92 Power Transistors | 2721-2N2222A-ND | 6

Amazon

5 mm Steel Ball Bearing (Boca Bearing) | SMR115-ZZ #5 LD | 2
9-22mm 1/3" F1.4 M12-mount lens with IR filter (Xenocam) | SPM16214000924 | 1
USB 2.0 Type-A Male to Mini-B 5pin Male Cable (Monoprice) | 844660054498 | 1
0.33-Inch Varifocal lens 2.8-12mm F1.3 Auto Iris (Computar) | TG4Z2813FCS-IR | 1
3 mm UV light, 395-400nm (Chanzon) | 100F3T-YT-WH-PU | 1 (Pack of 100)
5 mm super-bright IR LED, 940nm (Adafruit) | ADA388 | 1 (Pack of 25)
24 AWG 50 feet Electrical Wire (Fermerry) | Fermerry-39 | 1
Arduino Mega 2560 Rev3 Microcontroller Board (Arduino) | A000067 | 1
USB 2.0 Cable Type A/B (Arduino) | M000006 | 1
PCB Mount Screw Terminal Block Connectors (Tnisesm) | CATN-T03B | 1
Real Time Clock Module DS3231 AT24C32 IIC (Adeept) | 2pcsDS3231 | 1 (Pack of 2)
3V Lithium Battery (Junpower) | CR2032 | 1 (Pack of 10)
Heat Shrink Tubing (Electfun) | ELECFUN | 1
Black Adhesive contact paper (Yancorp) | 707516138165 | 1

IPS Weld-On 3 Acrylic Plastic Cement (Weld-On) | TLLPN-21847771 | 1
12V 5A DC Power Cable Male Female Connector (Centro Power) | DCCORD-MF | 1 (Pack of 10)
12V DC Power Connector Barrel Adaptor (Centro Power) | DCPLUG-MF | 1 (Pack of 10)
12V Red LED Flexible Strip Ribbon Light (Alitrove) | AL5RWPBK12V | 1
Power Strip Surge Protector 10Ft (Mifaso Power) | MFS311T | 1
Anti Vibration Pads (Empire of Electronics) | EOEPAD1 | 1 (Pack of 4)
1" x 12" x 12" Sound Absorption Wall Panels | 4348494783 | 1 (Pack of 24)
4 inch Zip Ties with 18 lb Tensile Strength (TANTTI) | KS-Onlytime-B541 | 1 (Pack of 200)
3M Scotch Super 33+ Electrical Tape - 3/4 in x 52 ft (Scotch) | 33+SUPER-3/4X52FT | 1
Hirose 4 Pin Female HR10A-7P-4S to Flying Leads Power Cable (Alvin’s Cables) | N/A | 1

Custom Parts

Rotary Encoder Adaptor (Aluminum 304) | CNC Machining (eMachineShop) | 1
Head Plate Holder (Aluminum 304) | CNC Machining (eMachineShop) | 2
Head Plate (Top Piece) (Aluminum 304) | CNC Machining (eMachineShop) | 1
Head Plate (Bottom Piece) (Aluminum 304) | CNC Machining (eMachineShop) | 1
Head rings (Aluminum 6061-T6) | CNC Machining (eMachineShop) | X
Rotary Wheel (1/8 Thick Clear Cast Acrylic) | Laser Cutting (Ponoko) | 2
Rotary Wheel Curved Surface (Clear Cast Acrylic) | Laser Cutting / Manual Cutting | 1
Rotary Wheel Curved Surface (Black Adhesive Contact Paper) | Laser Cutting / Manual Cutting | 1
Waste Management Ramp (Resin) | 3-D Printing (Craftcloud3d) | 1
Arduino Mega 2560 Rev3 Protective Case | 3-D Printing (Craftcloud3d) | 1
Arduino Mega 2560 Rev3 Shield SMT PCB | PCB Manufacturing (JLC PCB) | 1

FLIR

Firefly S Camera | FFY-U3-16S2M-S | 1
Tripod Adapter for Firefly S Camera | ACC-01-0017 | 1
USB 3.1 Locking Cable | ACC-01-2300 | 1
GPIO cable w/ 6 pins | ACC-01-3015 | 1

The Imaging Source

USB 2.0 CMOS Monochrome Camera | DMK-22BUC03 | 1

SYSRACKS

15U 35" Depth Under Desk Sound Proof Server Cabinet | SP15.900 | 1

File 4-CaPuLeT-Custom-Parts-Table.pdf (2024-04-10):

Custom Part and Filetype: | 3-D Rendering

Rotary Encoder Adaptor RotaryEncoderAdapter.step

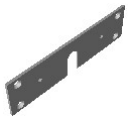
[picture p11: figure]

Head Plate (Bottom) HeadPlateBottomThreaded.sldprt

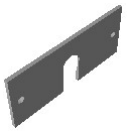
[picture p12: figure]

Head Plate (Top) HeadPlateTop.step

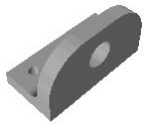
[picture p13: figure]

Head Plate Holder HeadPlateHolderThreaded.sldprt

Head Ring Headring.step

Custom Part and Filetype: | 3-D Rendering

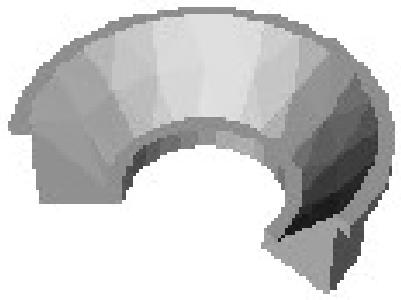
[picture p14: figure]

Head Ring (Five-Eighths Cut) HeadringFiveEighthsCut.step

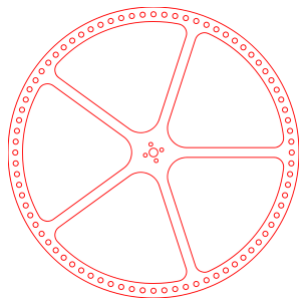
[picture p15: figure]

Treadmill Wheel TreadmillWheel.svg

Treadmill Wheel Curved Surface TreadmillWheelCurvedSurface.svg

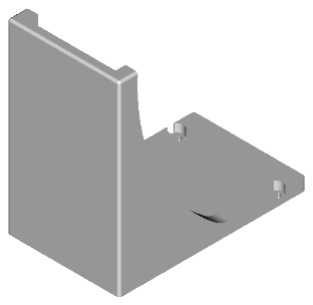
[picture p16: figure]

Waste Management Wheel WasteManagementRamp.step

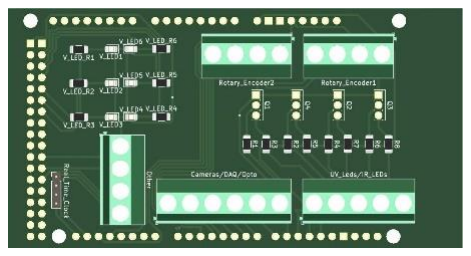
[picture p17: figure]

Arduino Mega 2560 Rev3 Compatible PCB SurfaceMountPCB.Kicad

Custom Part and Filetype: | 3-D Rendering

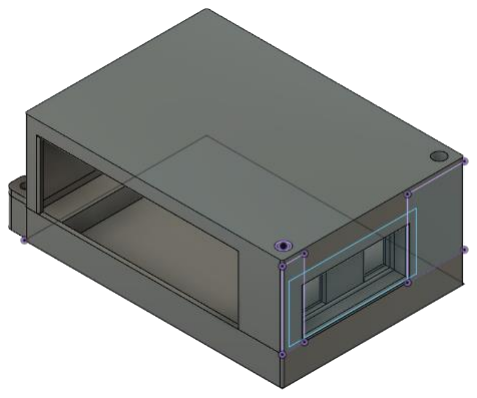
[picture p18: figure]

Arduino Mega 2560 Rev3 Protective Case ArduinoProtectiveCase.step


FireFly Tripod Adaptor FireFlyTripodAdaptor.dxf

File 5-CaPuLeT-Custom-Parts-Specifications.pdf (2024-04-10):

Our pupillometry wheel set-up requires five custom parts made from Aluminum 304 and Aluminum 6061-T6. These components fit securely to the optical posts we purchased from Thorlabs. We ordered them from eMachineShop, using the following files:
- Headring.step / Headring_mod_five_eighths. step
- HeadPlateTop. step
- RotaryEncoderAdapter. step
- HeadPlateHolderThreaded. sldprt
- HeadPlateBottomThreaded.sldprt
| Itemized Cost
Rotary Encoder | $28.43
Head Plate Holder (Set of 2) | $60.44
Head Plate Holder Top | $39.14
Head Plate Holder Bottom | $51.01
Head Ring | $5.16
Table 1. The eMachineShop quotes for the five custom components, obtained in June 2023. When submitting a quote through eMachineShop for custom CNC machining, you will be asked to “Specify threading and tolerances in a PDF, PNG or JPG”. The following screenshots from Fusion 360, with the accompanying description, will ensure that the two components are properly threaded.

| Material | L x W x H (Inches) | Tolerance (Inches)
Rotary Encoder | Aluminum 304 | 0.590” x 0.157” x 2.559” | +/- 0.005"
Head Plate Holder | | 1.184’’ x 0.595’’ x 0.667’’
Head Plate Holder Top | | 2.755” x 0.118” x 1.181”
Head Plate Holder Bottom | | 4.330” x 0.118” x 1.181”
Head Ring | Aluminum 6061-T6 | 0.475" x 0.472" x 0.130"
Table 2. The dimensions of each machined component in inches.
| Material | L x W x H (Centimeters) | Tolerance (Centimeters)
Rotary Encoder | Aluminum 304 | 1.498 x 0.398 x 6.50 | +/- 0.0127
Head Plate Holder | | 3.007 x 1.511 x 1.694
Head Plate Holder Top | | 6.997 x 0.299 x 2.999
Head Plate Holder Bottom | | 10.998 x 0.299 x 2.999
Head Ring | Aluminum 6061-T6 | 1.206 x 1.198 x 0.330
Table 3. The dimensions of each machined component in centimeters.
| Material | L x W x H (Millimeters) | Tolerance (Millimeters)
Rotary Encoder | Aluminum 304 | 14.98 x 3.98 x 65 | +/- 0.0127
Head Plate Holder | | 30.07 x 15.11 x 16.94
Head Plate Holder Top | | 69.97 x 2.99 x 29.99
Head Plate Holder Bottom | | 109.98x 2.99 x 29.99
Head Ring | Aluminum 6061-T6 | 12.06 x 11.98 x 3.30
Table 4. The dimensions of each machined component in millimeters.


The two holes closest to the center of the plate of the “HeadPlateBottomThreaded.sldprt” file are each internally threaded with size 3 mm threads (ISO Metric profile, thread tolerance 6H, right hand direction).


The two 0.396 cm diameter holes along the base of the “HeadPlateHolderThreaded.sldprt” file are each internally threaded with size 3 mm threads (ISO Metric profile, thread tolerance 6H, right hand direction).

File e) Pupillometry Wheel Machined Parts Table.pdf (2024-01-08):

Custom Part and Filetype: | 3-D Rendering

Rotary Encoder Adaptor RotaryEncoderAdapter.step


Head Plate (Bottom) HeadPlateBottomThreaded.sldprt


Head Plate Holder (Top) HeadPlateTop.step


Head Plate Holder HeadPlateHolderThreaded.sldprt

Head Ring Headring.step

Custom Part and Filetype: | 3-D Rendering


Head Ring (Five-Eighths Cut) Headring_five_eighths.step


Rotary Wheel RotaryWheel.svg

Rotary Wheel Curved Surface RotaryWheelCurvedSurface.svg


Waste Management Wheel WasteManagementRamp.step


Arduino Mega 2560 Rev3 Compatible PCB SurfaceMountPCB.Kicad

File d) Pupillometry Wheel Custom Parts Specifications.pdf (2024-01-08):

Our pupillometry wheel set-up requires five custom parts made from Aluminum 304 and Aluminum 6061-T6. These components fit securely to the optical posts we purchased from Thorlabs. We ordered them from eMachineShop, using the following files:
- Headring.STEP
- HeadPlateTop.STEP
- RotaryEncoderAdapter.STEP
- HeadPlateHolderthreaded.STEP
- HeadPlateBottomthreaded.STEP
| Material | L x W x H (Inches) | Tolerance (Inches)
Rotary Encoder | Aluminum 304 | 0.590” x 0.157” x 2.559” | +/- 0.005"
Head Plate Holder | | 1.184’’ x 0.595’’ x 0.667’’
Head Plate Holder Top | | 2.755” x 0.118” x 1.181”
Head Plate Holder Bottom | | 4.330” x 0.118” x 1.181”
Head Ring | Aluminum 6061-T6 | 0.475" x 0.472" x 0.130"

Table 1. The dimensions of each machined component in inches.

| Material | L x W x H (Centimeters) | Tolerance (Centimeters)
Rotary Encoder | Aluminum 304 | 1.498 x 0.398 x 6.50 | +/- 0.0127
Head Plate Holder | | 3.007 x 1.511 x 1.694
Head Plate Holder Top | | 6.997 x 0.299 x 2.999
Head Plate Holder Bottom | | 10.998 x 0.299 x 2.999
Head Ring | Aluminum 6061-T6 | 1.206 x 1.198 x 0.330

Table 2. The dimensions of each machined component in centimeters.

| Itemized Cost
Rotary Encoder | $28.43
Head Plate Holder (Set of 2) | $60.44
Head Plate Holder Top | $39.14
Head Plate Holder Bottom | $51.01
Head Ring | $5.16
Table 3. The eMachineShop quotes for the five custom components, obtained in June 2023.

When submitting a quote through eMachineShop for custom CNC machining, you will be asked to “Specify threading and tolerances in a PDF, PNG or JPG”. The following screenshots from Fusion 360, with the accompanying description, will ensure that the two components are properly threaded.


The two holes closest to the center of the plate of the “HeadPlateBottomThreaded.SLDPRT” file are each internally threaded with size 3 mm threads (ISO Metric profile, thread tolerance 6H, right hand direction).


The two 0.396 cm diameter holes along the base of the “HeadPlateHolderThreaded.SLDPRT” file are each internally threaded with size 3 mm threads (ISO Metric profile, thread tolerance 6H, right hand direction).

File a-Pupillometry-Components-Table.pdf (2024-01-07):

Part Name | Part / Identification Number | Quantity Needed Per Box

McMaster

5 mm Linear Motion Shaft | 6112K37 | 1
Clear polycarbonate film (Wraps around wheel) | 85585K15 | 1
Female Threaded Round Standoff | 93330A541 | 10
Black Screws (Secures top and bottom headplates) | 91290A111 | 2

Pololu

Aluminum Mounting Hub for 5mm Shaft | 1203 | 1 (Pack of 2)
s holding bearing holder | 1962 | 1

Thorlabs

0.75 Inch Post | TR075 | 1
2 Inch Post | TR2 | 2
4 Inch Post | TR4 | 5
6 Inch Post | TR6 | 2
8 Inch Post | TR8 | 2
10 Inch Post | TR10 | 2
2 Inch Post Holder | PH2 | 1
3 Inch Post Holder | PH3 | 4
6 Inch Post Holder | PH6 | 1
Right Angle End Clamp | RA180 | 4
Rotating Clamp | SWC | 1
Right Angle Post Clamp | RA90TR | 1
Mini Optical Post | MS3R | 1
12” x 18” Aluminum Breadboard | MB1218 | 1
Breadboard lifting handles | BBH1 | 2
Cap screws for holding female post | SH4S038 | 10

Thumbscrews for securing ball bearings | TS25H | 2

SparkFun

Rotary Encoder (Resin Coupling Adaptor Included) | E6B2-CWZ3E (E69-C06B) | 1

Digikey

Speaker 80hm 5w top port 104db | 2104-SP500208-3-ND | 1

Amazon

5 mm Steel Ball Bearing (Boca Bearing) | SMR115-ZZ #5 LD | 2
S-mount lens with IR filter (Xenocam) | SPM16214000924 | 1
Mini-USB 2.0 Type A to Mini-B cable (VOTY ) | B07NJW2ZPJ | 1 (Pack of 2)
0.33-Inch Varifocal lens 2.8-12mm F1.3 Auto Iris (Computar) | B002HRE2ZS / TG4Z2813FCS-IR | 1
3 mm UV light, 395-400nm (Chanzon) | 100F3T-YT-WH-PU | 1 (Pack of 100)
5 mm super-bright IR LED, 940nm (Adafruit) | ADA388 / B00ULB0U44 | 1 (Pack of 25)
24 AWG 50 feet Electrical Wire (Fermerry) | B089CX3FVV | 1
Arduino Mega 2560 Rev3 Microcontroller Board (Arduino) | A000067 / B0046AMGW0 | 1
USB 2.0 Cable Type A/B (Arduino) | M000006 / B013EOQUAW | 1
2.54mm Pitch Single Row Pin Header Strip (HiLetgo) | B07R5QDL8D | 1
PCB Mount Screw Terminal Block Connectors (Tnisesm) | CATN-T03B | 1
2N2222 NPN TO-92 Power Transistors (Ardest) | B07222XY81 | 1 (Pack of 100)
Real Time Clock Module DS3231 AT24C32 IIC (Adeept) | 2pcsDS3231 / B097PMNMQZ | 1 (Pack of 2)
3V Lithium Battery (Junpower) | CR2032 / B07LGL9LQ1 | 1 (Pack of 10)
Heat Shrink Tubing (Electfun) | ELECFUN / B08SQBPVJB | 1
Black Adhesive contact paper (Yancorp) | B082CPSVPW | 1
IPS Weld-On 3 Acrylic Plastic Cement (Weld-On) | TLLPN-21847771 | 1
12V 5A DC Power Cable Male Female Connector (Centro Power) | B07C7VSRBG | 1 (Pack of 10)
12V DC Power Connector Barrel Adaptor (Centro Power) | B07C61434H | 1 (Pack of 10)
12V Red LED Flexible Strip Ribbon Light (Alitrove) | B07MXXDWDM | 1
Power Strip Surge Protector 10Ft (Mifaso Power) | B0BTPB5Z4W | 1

Anti Vibration Pads (Functional Necessities) | B08NWRFLDC | 1 (Pack of 4)
1" x 12" x 12" Sound Absorption Wall Panels (Xin & Log) | B078VVJTXQ | 1 (Pack of 24)
4 inch Zip Ties with 18 lb Tensile Strength | B0BC1VH4XB | 1 (Pack of 200)

Custom Parts

Rotary Encoder Adaptor (Aluminum 304) | CNC Machining (eMachineShop) | 1
Head Plate Holder (Aluminum 304) | CNC Machining (eMachineShop) | 2
Head Plate (Top Piece) (Aluminum 304) | CNC Machining (eMachineShop) | 1
Head Plate (Bottom Piece) (Aluminum 304) | CNC Machining (eMachineShop) | 1
Head rings (Aluminum 6061-T6) | CNC Machining (eMachineShop) | X
Rotary Wheel (1/8 Thick Clear Cast Acrylic) | Laser Cutting (Ponoko) | 2
Rotary Wheel Curved Surface (Clear Cast Acrylic) | Laser Cutting / Manual Cutting | 1
Rotary Wheel Curved Surface (Black Adhesive Contact Paper) | Laser Cutting / Manual Cutting | 1
Waste Management Ramp (Resin) | 3-D Printing (Craftcloud3d) | 1
Arduino Mega 2560 Rev3 Compatible PCB (Surface-Mount Technology Printed Circuit Board) | PCB Manufacturing (JLC PCB) | 1

FLIR

Firefly S Camera | FFY-U3-16S2M-S | 1
Tripod Adapter for Firefly S Camera | ACC-01-0017 | 1
USB 3.1 Locking Cable | ACC-01-2300 | 1
GPIO cable w/ 6 pins | ACC-01-3015 | 1

The Imaging Source

USB 2.0 CMOS Monochrome Camera | DMK-22BUC03 | 1

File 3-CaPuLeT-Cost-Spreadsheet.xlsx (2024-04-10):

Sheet: Parts Built In-House
Part Number | Distributor | Part Name | Distributor Part Number | Qty Needed | Unit Price | Total Price
1 | McMaster-Carr | 5 mm Linear Motion Shaft | 6112K37 | 1 | $10.98 | $10.98
2 | McMaster-Carr | Clear Impact-Resistant Polycarbonate Film | 85585K15 | 1 | $8.35 | $8.35
3 | McMaster-Carr | Female Threaded Round Standoff | 93330A541 | 10 | $2.13 | $21.30
4 | McMaster-Carr | Socket Head Screw M3 x 0.5 mm Thread, 6 mm Long | 91290A111 | 1 (Pack of 100) | $10.91 | $10.91
5 | Polulu | Aluminum Mounting Hub for 5mm Shaft | 1203 | 1 (Pack of 2) | $18.90 | $18.90
6 | Polulu | Machine Screw: #4-40, 1/2″ Length, Phillips | 1962 | 1 (Pack of 25) | $1.39 | $1.39
7 | Thorlabs | 0.75 Inch Post | TR075 | 1 | $5.38 | $5.38
8 | Thorlabs | 2 Inch Post | TR2 | 2 | $5.90 | $11.80
9 | Thorlabs | 3 Inch Post | TR3 | 2 | $6.15 | $12.30
10 | Thorlabs | 4 Inch Post, 5 Pack | TR4-P5 | 1 (Pack of 5) | $30.00 | $30.00
11 | Thorlabs | 6 Inch Post | TR6 | 2 | $8.09 | $16.18
12 | Thorlabs | 8 Inch Post | TR8 | 2 | $9.69 | $19.38
13 | Thorlabs | 10 Inch Post | TR10 | 2 | $10.76 | $21.52
14 | Thorlabs | 2 Inch Post Holder | PH2 | 1 | $8.95 | $8.95
15 | Thorlabs | 3 Inch Post Holder | PH3 | 4 | $9.62 | $38.48
16 | Thorlabs | 6 Inch Post Holder | PH6 | 1 | $14.70 | $14.70
17 | Thorlabs | Right Angle End Clamp | RA180 | 4 | $12.34 | $49.36
18 | Thorlabs | Rotating Clamp | SWC | 1 | $26.91 | $26.91
19 | Thorlabs | Right Angle Post Clamp | RA90TR | 1 | $17.82 | $17.82
20 | Thorlabs | Mini Optical Post | MS3R | 1 | $9.09 | $9.09
21 | Thorlabs | Aluminum Breadboard 8" x 10" x 1/2", 1/4"-20 Taps | MB810 | 1 | $131.60 | $131.60
22 | Thorlabs | Aluminum Breadboard 12" x 18" x 1/2", 1/4"-20 Taps | MB1218 | 1 | $214.65 | $214.65
23 | Thorlabs | Breadboard Lifting Handles, Reinforced Polymer | BBH1 | 2 (Pack of 2) | $17.01 | $17.01
24 | Thorlabs | 4-40 Stainless Steel Cap Screw, 3/8" Long | SH4S038 | 1 (Pack of 50) | $9.31 | $9.31
25 | Thorlabs | Spring-Loaded 3/16" Hex-Locking Thumbscrew, 1/4"-20 Thread | TS25H | 2 | $2.87 | $5.74
26 | Thorlabs | 1/4"-20 Stainless Steel Setscrew, 5/8" Long (Adaptor) | SS25S0625 | 1 (Pack of 25) | $6.97 | $6.97
27 | Thorlabs | 1/4" Washer, M6 Compatible, Stainless Steel | W25S050 | 1 (Pack of 100) | $10.20 | $10.20
28 | Thorlabs | 1/4"-20 Stainless Steel Nut | N25S0440 | 1 (Pack of 50) | $6.43 | $6.43
29 | SparkFun | Rotary Encoder - 1024 P/R (Quadrature) | E6B2-CWZ3E (E69-C06B) | 1 | $48.50 | $48.50
30 | Digikey | Speaker 80hm 5 w top port 104db | 2104-SP500208-3-ND | 1 | $6.79 | $6.79
31 | Digikey | 2.54mm Pitch Single Row Pin Header Strip | S1012EC-40-ND | 1
32 | Digikey | 2N2222 NPN TO-92 Power Transistors | 2721-2N2222A-ND | 1
33 | Amazon | 5 mm Steel Ball Bearing | SMR115-ZZ #5 LD | 2 | $10.58 | $21.16
34 | Amazon | S-mount lens with IR filter (Xenocam) | SPM16214000924 | 1 | $19.99 | $19.99
35 | Amazon | USB 2.0 Type-A Male to Mini-B 5pin Male Cable (Monoprice) | 844660054498 | 1 | $4.78 | $4.78
36 | Amazon | 0.33-Inch Varifocal lens 2.8-12mm F1.3 Auto Iris (Computar) | TG4Z2813FCS-IR | 1 (Used) | $19.99 | $19.99
37 | Amazon | 3 mm UV light, 395-400nm (Chanzon) | 100F3T-YT-WH-PU | 1 (Pack of 100) | $6.99 | $6.99
38 | Amazon | 5 mm super-bright IR LED, 940nm (Adafruit) | ADA388 | 1 (Pack of 25) | $10.98 | $10.98
39 | Amazon | 24 AWG 50 feet Electrical Wire (Fermerry) | Fermerry-39 | 1 | $26.99 | $26.99
40 | Amazon | Arduino Mega 2560 Rev3 Microcontroller Board (Arduino) | A000067 | 1 | $48.99 | $48.99
41 | Amazon | USB 2.0 Cable Type A/B (Arduino) | M000006 | 1 | $7.00 | $7.00
42 | Amazon | PCB Mount Screw Terminal Block Connectors (Tnisesm) | CATN-T03B | 1 | $8.99 | $8.99
43 | Amazon | Real Time Clock Module DS3231 AT24C32 IIC (Adeept) | 2pcsDS3231 | 1 (Pack of 2) | $7.99 | $7.99
44 | Amazon | 3V Lithium Battery (Junpower) | CR2032 | 1 (Pack of 10) | $4.99 | $4.99
45 | Amazon | Heat Shrink Tubing (Electfun) | ELECFUN | 1 | $14.99 | $14.99
46 | Amazon | Black Adhesive contact paper (Yancorp) | 707516138165 | 1 | $6.98 | $6.98
47 | Amazon | IPS Weld-On 3 Acrylic Plastic Cement (Weld-On) | TLLPN-21847771 | 1 | $28.55 | $28.55
48 | Amazon | 12V 5A DC Power Cable Male Female Connector (Centro Power) | DCCORD-MF | 1 (Pack of 10) | $9.19 | $9.19
49 | Amazon | 12V DC Power Connector Barrel Adaptor (Centro Power) | DCPLUG-MF | 1 (Pack of 10) | $7.99 | $7.99
50 | Amazon | 12V Red LED Flexible Strip Ribbon Light (Alitrove, 16.4 feet) | AL5RWPBK12V | 1 | $13.99 | $13.99
51 | Amazon | Power Strip Surge Protector 10Ft (Mifaso Power) | MFS311T | 1 | $19.99 | $19.99
52 | Amazon | Anti Vibration Pads (Functional Necessities) | EOEPAD1 | 1 (Pack of 4) | $14.99 | $14.99
53 | Amazon | 1" x 12" x 12" Sound Absorption Wall Panels (Xin & Log) | 4348494783 | 1 (Pack of 24) | $17.99 | $17.99
54 | Amazon | 4 inch Zip Ties with 18 lb Tensile Strength | KS-Onlytime-B541 | 1 (Pack of 200) | $3.99 | $3.99
55 | Amazon | 3M Scotch Super 33+ Electrical Tape - 3/4 in x 52 ft | 33+SUPER-3/4X52FT | 1 | $4.98 | $4.98
56 | Custom Machined Parts | Rotary Encoder Adaptor (Aluminum 304) | CNC Machining (eMachineShop) | 6 (Bulk Purchase) | $28.43 | $170.62
57 | Custom Machined Parts | Head Plate Holder (Aluminum 304) | CNC Machining (eMachineShop) | 12 (Bulk Purchase) | $30.20 | $362.44
58 | Custom Machined Parts | Head Plate (Top Piece) (Aluminum 304) | CNC Machining (eMachineShop) | 6 (Bulk Purchase) | $39.14 | $234.85
59 | Custom Machined Parts | Head Plate (Bottom Piece) (Aluminum 304) | CNC Machining (eMachineShop) | 6 (Bulk Purchase) | $51.01 | $306.04
60 | Custom Machined Parts | Head rings (Aluminum 6061-T6) | CNC Machining (eMachineShop) | 100 (Bulk Purchase) | $5.16 | $258.22
61 | Custom Machined Parts | Rotary Wheel (1/8 Thick Clear Cast Acrylic) | Laser Cutting (Ponoko) | 2 | $0.00 | $0.00
62 | Custom Machined Parts | Rotary Wheel Curved Surface (Clear Cast Acrylic) | Laser Cutting / Manual Cutting | 1 | $0.00 | $0.00
63 | Custom Machined Parts | Rotary Wheel Curved Surface (Black Adhesive Contact Paper) | Laser Cutting / Manual Cutting | 1 | $0.00 | $0.00
64 | Custom Machined Parts | Waste Management Ramp (Resin) | 3-D Printing (Craftcloud3d) | 1 | $0.00 | $0.00
65 | Custom Machined Parts | Arduino Protective Case (Resin) | 3-D Printing (Craftcloud3d) | 1 | $0.00 | $0.00
66 | Custom Machined Parts | Arduino Mega 2560 Rev3 Shield SMT PCB | PCB Manufacturing (JLC PCB) | 1 | X | X
67 | FLIR | Firefly S Camera | FFY-U3-16S2M-S | 1 | $234.00 | $234.00
68 | FLIR | Tripod Adapter for Firefly S Camera | ACC-01-0017 | 1 | $32.10 | $32.10
69 | FLIR | USB 3.1 Locking Cable | ACC-01-2300 | 1 | $24.60 | $24.60
70 | FLIR | GPIO cable w/ 6 pins | ACC-01-3015 | 1 | $9.60 | $9.60
71 | The Imaging Source | USB 2.0 CMOS Monochrome Camera | DMK-22BUC03 | 1 | $234.00 | $234.00
72 | SYSRACKS | 15U 35" Depth Under Desk Sound Proof Server Cabinet | SP15.900 | 1 | $1122.00 | $1122.00

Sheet: Parts Custom Ordered
Part Number | Distributor | Part Name | Distributor Part Number | Qty Needed | Unit Price | Total Price
1 | McMaster-Carr | 5 mm Linear Motion Shaft | 6112K37 | 1 | $10.98 | $10.98
2 | McMaster-Carr | Clear Impact-Resistant Polycarbonate Film | 85585K15 | 1 | $8.35 | $8.35
3 | McMaster-Carr | Female Threaded Round Standoff | 93330A541 | 10 | $2.13 | $21.30
4 | McMaster-Carr | Socket Head Screw M3 x 0.5 mm Thread, 6 mm Long | 91290A111 | 1 (Pack of 100) | $10.91 | $10.91
5 | Polulu | Aluminum Mounting Hub for 5mm Shaft | 1203 | 1 (Pack of 2) | $18.90 | $18.90
6 | Polulu | Machine Screw: #4-40, 1/2″ Length, Phillips | 1962 | 1 (Pack of 25) | $1.39 | $1.39
7 | Thorlabs | 0.75 Inch Post | TR075 | 1 | $5.38 | $5.38
8 | Thorlabs | 2 Inch Post | TR2 | 2 | $5.90 | $11.80
9 | Thorlabs | 3 Inch Post | TR3 | 2 | $6.15 | $12.30
10 | Thorlabs | 4 Inch Post, 5 Pack | TR4-P5 | 1 (Pack of 5) | $30.00 | $30.00
11 | Thorlabs | 6 Inch Post | TR6 | 2 | $8.09 | $16.18
12 | Thorlabs | 8 Inch Post | TR8 | 2 | $9.69 | $19.38
13 | Thorlabs | 10 Inch Post | TR10 | 2 | $10.76 | $21.52
14 | Thorlabs | 2 Inch Post Holder | PH2 | 1 | $8.95 | $8.95
15 | Thorlabs | 3 Inch Post Holder | PH3 | 4 | $9.62 | $38.48
16 | Thorlabs | 6 Inch Post Holder | PH6 | 1 | $14.70 | $14.70
17 | Thorlabs | Right Angle End Clamp | RA180 | 4 | $12.34 | $49.36
18 | Thorlabs | Rotating Clamp | SWC | 1 | $26.91 | $26.91
19 | Thorlabs | Right Angle Post Clamp | RA90TR | 1 | $17.82 | $17.82
20 | Thorlabs | Mini Optical Post | MS3R | 1 | $9.09 | $9.09
21 | Thorlabs | Aluminum Breadboard 8" x 10" x 1/2", 1/4"-20 Taps | MB810 | 1 | $131.60 | $131.60
22 | Thorlabs | Aluminum Breadboard 12" x 18" x 1/2", 1/4"-20 Taps | MB1218 | 1 | $214.65 | $214.65
23 | Thorlabs | Breadboard Lifting Handles, Reinforced Polymer | BBH1 | 2 (Pack of 2) | $17.01 | $17.01
24 | Thorlabs | 4-40 Stainless Steel Cap Screw, 3/8" Long | SH4S038 | 1 (Pack of 50) | $9.31 | $9.31
25 | Thorlabs | Spring-Loaded 3/16" Hex-Locking Thumbscrew, 1/4"-20 Thread | TS25H | 2 | $2.87 | $5.74
26 | Thorlabs | 1/4"-20 Stainless Steel Setscrew, 5/8" Long (Adaptor) | SS25S0625 | 1 (Pack of 25) | $6.97 | $6.97
27 | Thorlabs | 1/4" Washer, M6 Compatible, Stainless Steel | W25S050 | 1 (Pack of 100) | $10.20 | $10.20
28 | Thorlabs | 1/4"-20 Stainless Steel Nut | N25S0440 | 1 (Pack of 50) | $6.43 | $6.43
29 | SparkFun | Rotary Encoder - 1024 P/R (Quadrature) | E6B2-CWZ3E (E69-C06B) | 1 | $48.50 | $48.50
30 | Digikey | Speaker 80hm 5 w top port 104db | 2104-SP500208-3-ND | 1 | $6.79 | $6.79
31 | Digikey | 2.54mm Pitch Single Row Pin Header Strip | S1012EC-40-ND | 3 | $0.51 | $1.53
32 | Digikey | 2N2222 NPN TO-92 Power Transistors | 2721-2N2222A-ND | 6 | $0.24 | $1.44
33 | Amazon | 5 mm Steel Ball Bearing | SMR115-ZZ #5 LD | 2 | $10.58 | $21.16
34 | Amazon | S-mount lens with IR filter (Xenocam) | SPM16214000924 | 1 | $19.99 | $19.99
35 | Amazon | USB 2.0 Type-A Male to Mini-B 5pin Male Cable (Monoprice) | 844660054498 | 1 | $4.78 | $4.78
36 | Amazon | 0.33-Inch Varifocal lens 2.8-12mm F1.3 Auto Iris (Computar) | TG4Z2813FCS-IR | 1 (Used) | $19.99 | $19.99
37 | Amazon | 3 mm UV light, 395-400nm (Chanzon) | 100F3T-YT-WH-PU | 1 (Pack of 100) | $6.99 | $6.99
38 | Amazon | 5 mm super-bright IR LED, 940nm (Adafruit) | ADA388 | 1 (Pack of 25) | $10.98 | $10.98
39 | Amazon | 24 AWG 50 feet Electrical Wire (Fermerry) | Fermerry-39 | 1 | $26.99 | $26.99
40 | Amazon | Arduino Mega 2560 Rev3 Microcontroller Board (Arduino) | A000067 | 1 | $48.99 | $48.99
41 | Amazon | USB 2.0 Cable Type A/B (Arduino) | M000006 | 1 | $7.00 | $7.00
42 | Amazon | PCB Mount Screw Terminal Block Connectors (Tnisesm) | CATN-T03B | 1 | $8.99 | $8.99
43 | Amazon | Real Time Clock Module DS3231 AT24C32 IIC (Adeept) | 2pcsDS3231 | 1 (Pack of 2) | $7.99 | $7.99
44 | Amazon | 3V Lithium Battery (Junpower) | CR2032 | 1 (Pack of 10) | $4.99 | $4.99
45 | Amazon | Heat Shrink Tubing (Electfun) | ELECFUN | 1 | $14.99 | $14.99
46 | Amazon | Black Adhesive contact paper (Yancorp) | 707516138165 | 1 | $6.98 | $6.98
47 | Amazon | IPS Weld-On 3 Acrylic Plastic Cement (Weld-On) | TLLPN-21847771 | 1 | $28.55 | $28.55
48 | Amazon | 12V 5A DC Power Cable Male Female Connector (Centro Power) | DCCORD-MF | 1 (Pack of 10) | $9.19 | $9.19
49 | Amazon | 12V DC Power Connector Barrel Adaptor (Centro Power) | DCPLUG-MF | 1 (Pack of 10) | $7.99 | $7.99
50 | Amazon | 12V Red LED Flexible Strip Ribbon Light (Alitrove, 16.4 feet) | AL5RWPBK12V | 1 | $13.99 | $13.99
51 | Amazon | Power Strip Surge Protector 10Ft (Mifaso Power) | MFS311T | 1 | $19.99 | $19.99
52 | Amazon | Anti Vibration Pads (Functional Necessities) | EOEPAD1 | 1 (Pack of 4) | $14.99 | $14.99
53 | Amazon | 1" x 12" x 12" Sound Absorption Wall Panels (Xin & Log) | 4348494783 | 1 (Pack of 24) | $17.99 | $17.99
54 | Amazon | 4 inch Zip Ties with 18 lb Tensile Strength | KS-Onlytime-B541 | 1 (Pack of 200) | $3.99 | $3.99
55 | Amazon | 3M Scotch Super 33+ Electrical Tape - 3/4 in x 52 ft | 33+SUPER-3/4X52FT | 1 | $4.98 | $4.98
56 | Amazon | Hirose 4 Pin Female HR10A-7P-4S to Flying Leads Power Cable (Alvin’s Cables) | N/A | 1 | $25.99 | $25.99
57 | Custom Machined Parts | Rotary Encoder Adaptor (Aluminum 304) | CNC Machining (eMachineShop) | 6 (Bulk Purchase) | $28.43 | $170.62
58 | Custom Machined Parts | Head Plate Holder (Aluminum 304) | CNC Machining (eMachineShop) | 12 (Bulk Purchase) | $30.20 | $362.44
59 | Custom Machined Parts | Head Plate (Top Piece) (Aluminum 304) | CNC Machining (eMachineShop) | 6 (Bulk Purchase) | $39.14 | $234.85
60 | Custom Machined Parts | Head Plate (Bottom Piece) (Aluminum 304) | CNC Machining (eMachineShop) | 6 (Bulk Purchase) | $51.01 | $306.04
61 | Custom Machined Parts | Head rings (Aluminum 6061-T6) | CNC Machining (eMachineShop) | 100 (Bulk Purchase) | $5.16 | $258.22
62 | Custom Machined Parts | Rotary Wheel (1/8 Thick Clear Cast Acrylic) | Laser Cutting (Ponoko) | 2 | $61.06 | $61.06
63 | Custom Machined Parts | Rotary Wheel Curved Surface (Clear Cast Acrylic) | Laser Cutting / Manual Cutting | 1 | $0.00 | $0.00
64 | Custom Machined Parts | Rotary Wheel Curved Surface (Black Adhesive Contact Paper) | Laser Cutting / Manual Cutting | 1 | $0.00 | $0.00
65 | Custom Machined Parts | Waste Management Ramp (Resin) | 3-D Printing (Craftcloud3d) | 1 | $57.76 | $57.76
66 | Custom Machined Parts | Arduino Mega 2560 Rev3 Protective Case (Resin) | 3-D Printing (Craftcloud3d) | 1 | $16.06 | $16.06
67 | Custom Machined Parts | Arduino Mega 2560 Rev3 Shield SMT PCB | PCB Manufacturing (JLC PCB) | 1 | X | X
68 | FLIR | Firefly S Camera | FFY-U3-16S2M-S | 1 | $234.00 | $234.00
69 | FLIR | Tripod Adapter for Firefly S Camera | ACC-01-0017 | 1 | $32.10 | $32.10
70 | FLIR | USB 3.1 Locking Cable | ACC-01-2300 | 1 | $24.60 | $24.60
71 | FLIR | GPIO cable w/ 6 pins | ACC-01-3015 | 1 | $9.60 | $9.60
72 | The Imaging Source | USB 2.0 CMOS Monochrome Camera | DMK-22BUC03 | 1 | $234.00 | $234.00
73 | SYSRACKS | 15U 35" Depth Under Desk Sound Proof Server Cabinet | SP15.900 | 1 | $1122.00 | $1122.00

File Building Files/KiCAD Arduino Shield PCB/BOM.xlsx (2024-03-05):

Comment | Designator | Footprint | JLCPCB Part #（optional）
1000 | R1,R6,R2,R4 | R_1206_3216Metric
300 | V_LED_R3,V_LED_R2,V_LED_R4,R3,R5,R7,V_LED_R1,V_LED_R5,V_LED_R6,R8 | R_1206_3216Metric
LED | V_LED4,V_LED6,V_LED1,V_LED2,V_LED3,V_LED5 | LED_0805_2012Metric

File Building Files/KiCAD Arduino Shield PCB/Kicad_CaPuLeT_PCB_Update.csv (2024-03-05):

Id | Designator | Footprint | Quantity | Designation | Supplier and ref
1 | A1 | Arduino_Mega2560_R3_Shield_Reduced_Hole | 1 | Arduino_Mega2560_R3_Shield
2 | Real_Time_Clock | PinHeader_1x04_P2.00mm_Vertical | 1 | Conn_01x04_Pin
3 | V_LED4,V_LED6,V_LED1,V_LED2,V_LED3,V_LED5 | LED_0805_2012Metric | 6 | LED
4 | UV_Leds/IR_LEDs | TerminalBlock_Phoenix_MKDS-1,5-5_1x05_P5.00mm_Horizontal | 1 | Screw_Terminal_01x05
5 | Rotary_Encoder1,Rotary_Encoder2,Other | TerminalBlock_Phoenix_MKDS-1,5-4_1x04_P5.00mm_Horizontal | 3 | Screw_Terminal_01x04
6 | R1,R6,R2,R4 | R_1206_3216Metric | 4 | 1000
7 | V_LED_R3,V_LED_R2,V_LED_R4,R3,R5,R7,V_LED_R1,V_LED_R5,V_LED_R6,R8 | R_1206_3216Metric | 10 | 300
8 | Q3,Q2,Q4,Q1 | SIPAK_Vertical | 4 | 2N2219
9 | Cameras/DAQ/Opto | TerminalBlock_Phoenix_MKDS-1,5-6_1x06_P5.00mm_Horizontal | 1 | Screw_Terminal_01x06

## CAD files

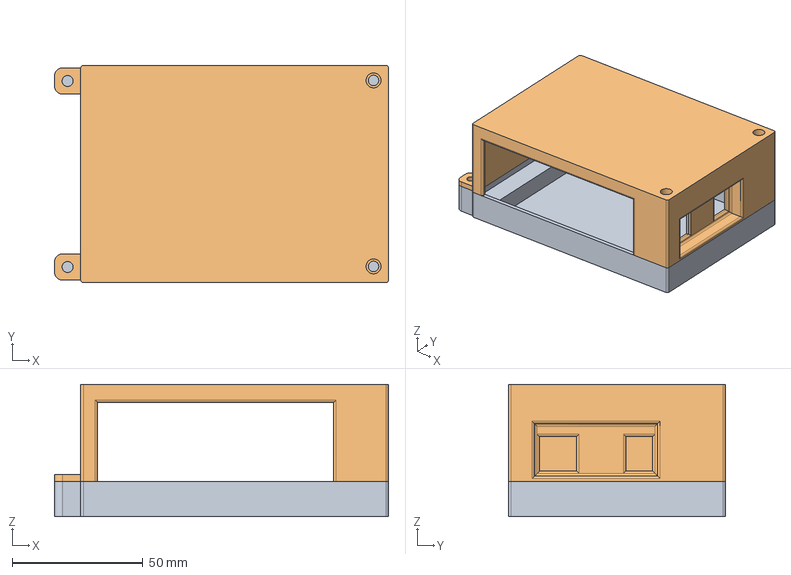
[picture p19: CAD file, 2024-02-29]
Building Files/ArduinoProtectiveCase.step
127.5 x 83.0 x 50.5 mm

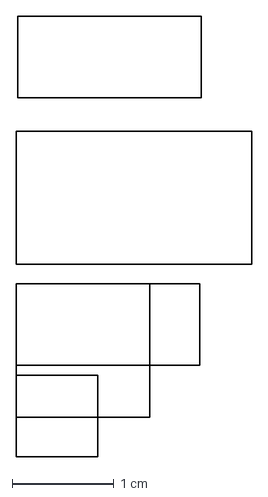
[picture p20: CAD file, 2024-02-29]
Building Files/FireflyTripodAdaptor.dxf
2.31 x 4.33 cm

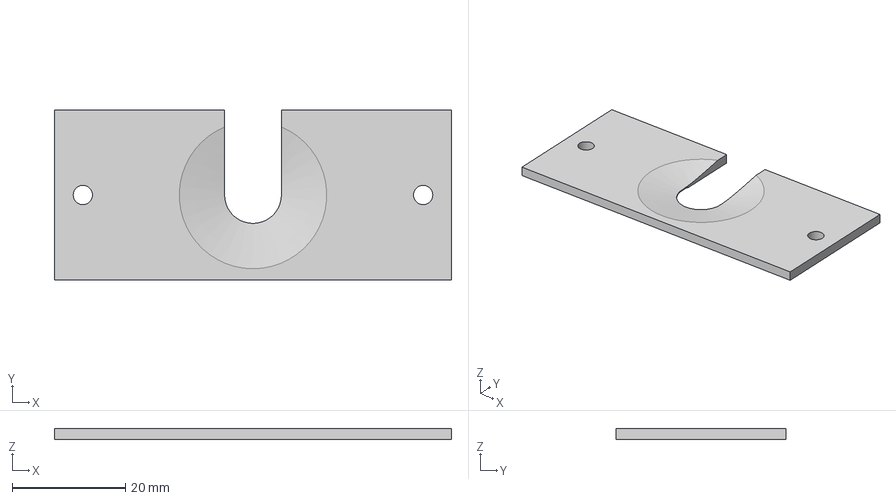
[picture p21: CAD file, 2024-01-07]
Building Files/HeadPlateTop.step
70.0 x 30.0 x 2.00 mm

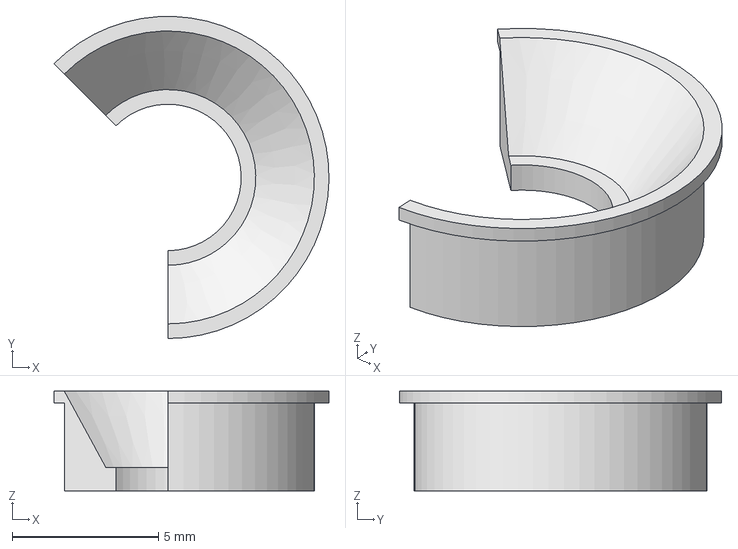
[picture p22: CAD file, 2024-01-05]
Building Files/HeadringFiveEighthsCut.step
9.39 x 11.0 x 3.40 mm

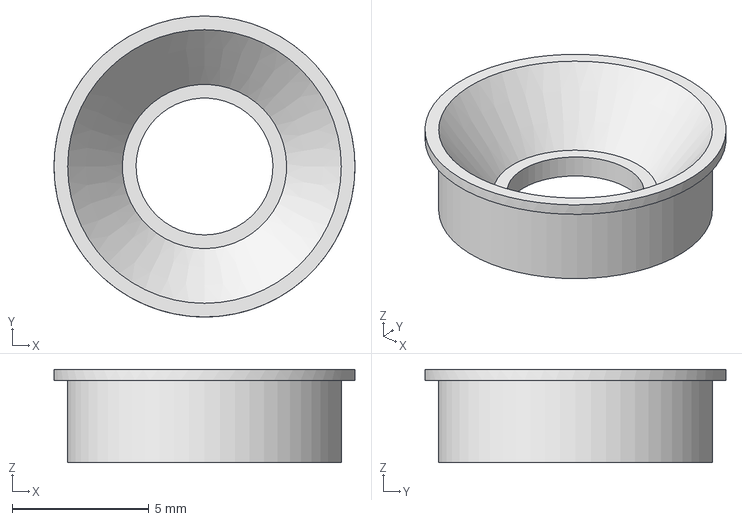
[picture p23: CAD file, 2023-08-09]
Building Files/Headring.step
11.0 x 11.0 x 3.40 mm

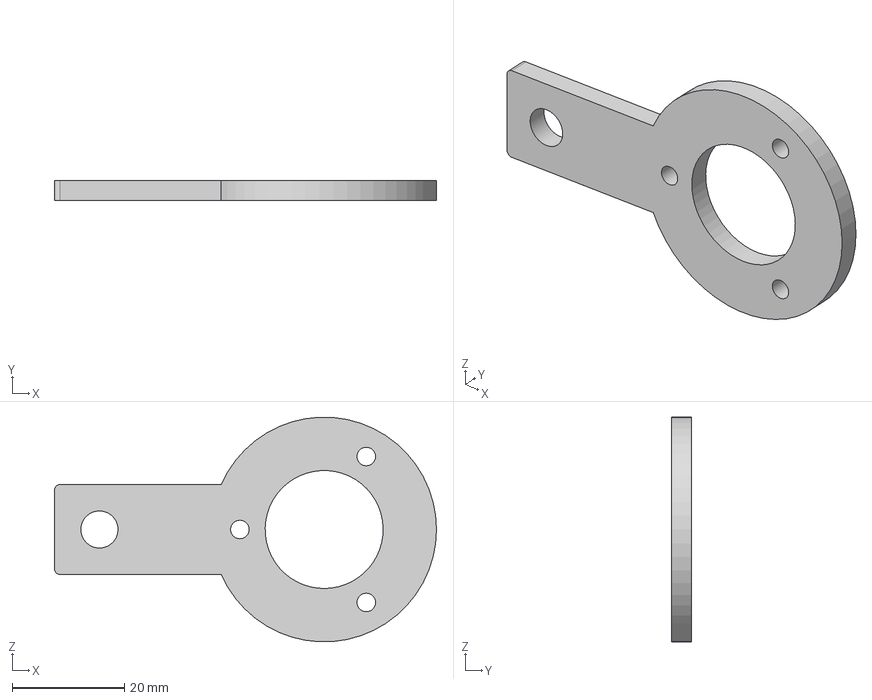
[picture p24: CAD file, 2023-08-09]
Building Files/RotaryEncoderAdapter.step
68.0 x 3.61 x 40.0 mm

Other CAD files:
Building Files/HeadPlateHolderThreaded.sldprt
Building Files/HeadPlateBottomThreaded.sldprt
Building Files/WasteManagementRamp.step

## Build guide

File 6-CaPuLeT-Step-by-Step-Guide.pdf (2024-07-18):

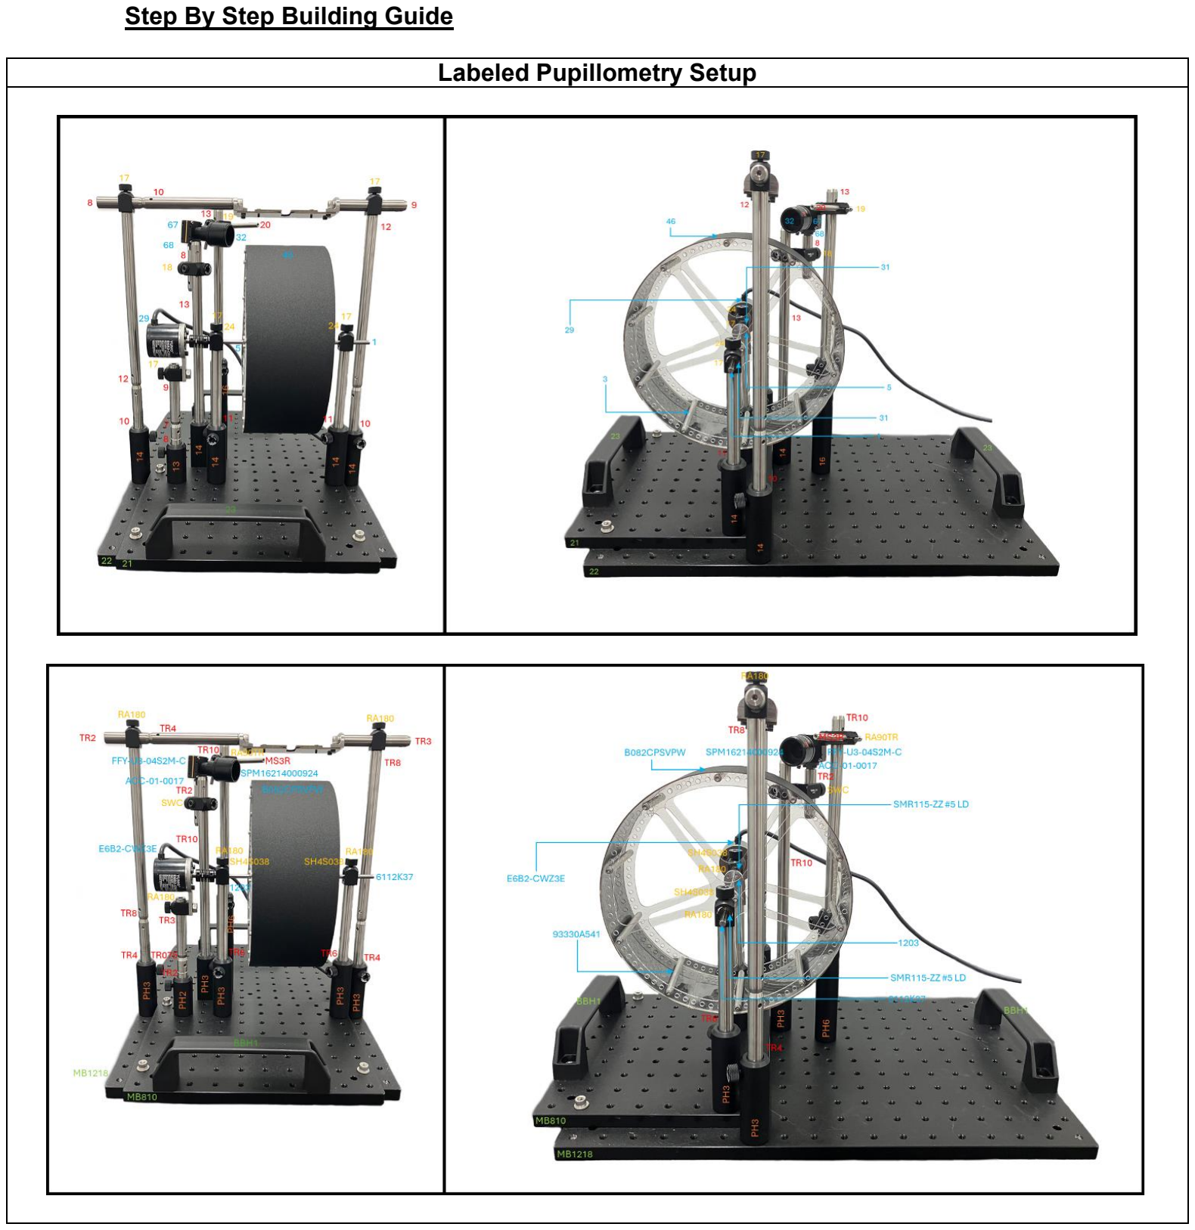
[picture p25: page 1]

Step By Step Building Guide

Labeled Pupillometry Setup

### Arduino Protective Cover

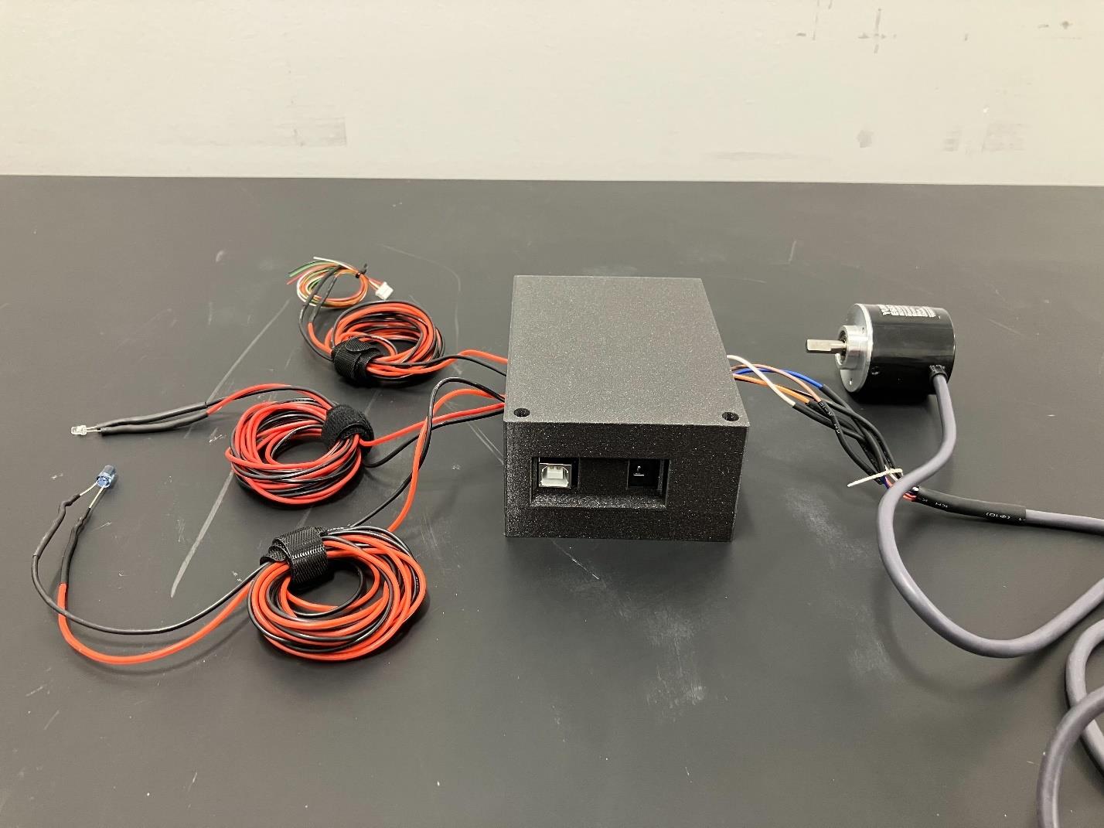
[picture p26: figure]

* The printed circuit board housed in the protective Arduino case, with the electrical components required for a single locomotion wheel setup. This includes the rotary encoder, low-power ultraviolet LED, infrared LED, and GPIO cable. After powering the Arduino Mega with a 5-V USB connection or with an external power supply.

Assemble the Breadboard
Single Breadboard Option | Modular Breadboard Option

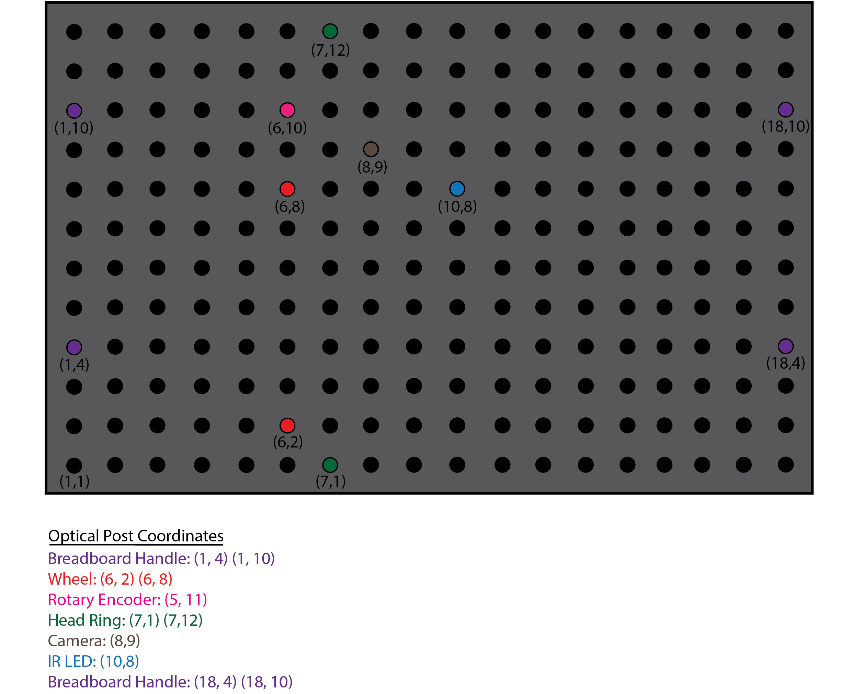
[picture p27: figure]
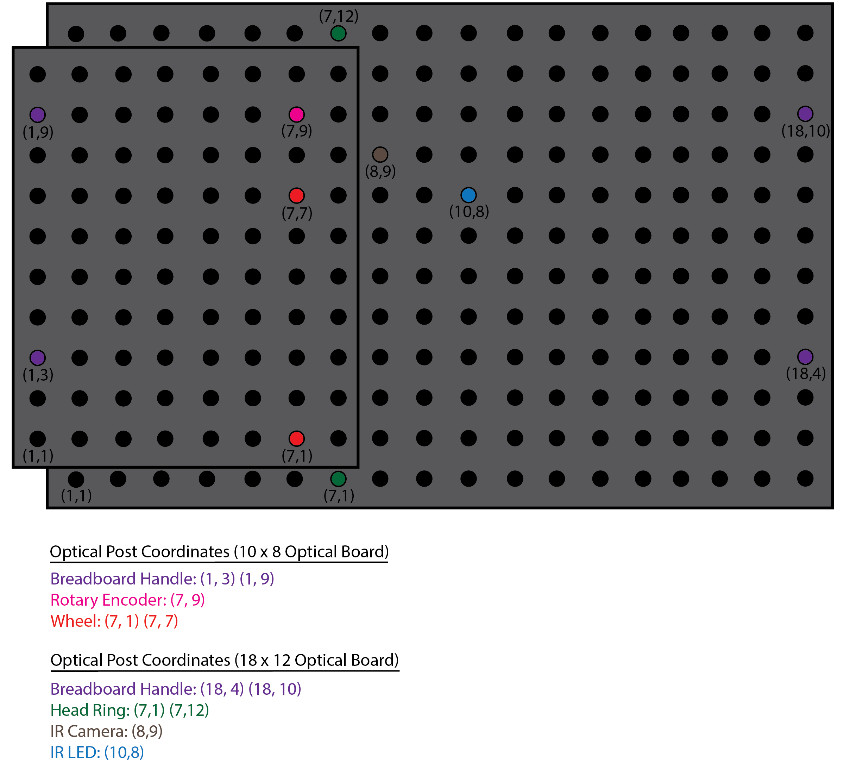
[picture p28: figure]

Assemble the Breadboard (Single Breadboard Option)
1. Mount post holders according to the above figure
a) Handle - Two SH4S038 screws at coordinates (1,4) and (1,10)
b) Wheel - Two PH3 post holders at coordinates (6,2) and (6,8)
c) Rotary encoder - One PH2 post holder at coordinate (5,11)
d) Head plate - Two PH3 post holder at coordinates (7,1) and (7,12)
e) IR Camera - One PH3 post holder at coordinate (8,9)
f) IR LED - One PH6 post holder at coordinate (10,8)
g) Handle - Two SH4S038 screws at coordinates (18,4) and (18,10)

Assemble the Breadboard (Singular and Modular Breadboard Option)
1. Mount post holders according to the singular breadboard option above
a. Handle - Two SH4S038 screws at coordinates (1,4) and (1,10)
b. Wheel - Two PH3 post holders at coordinates (6,2) and (6,8)
c. Rotary encoder - One PH2 post holder at coordinate (5,11)
d. Head plate - Two PH3 post holder at coordinates (7,1) and (7,12)
e. IR Camera - One PH3 post holder at coordinate (8,9)
f. IR LED - One PH6 post holder at coordinate (10,8)
g. Handle - Two SH4S038 screws at coordinates (18,4) and (18,10)
2. Mount post holders according to the modular breadboard option above
a. 10 x 8 Optical Board
- Handle - Two SH4S038 screws at coordinates (1,3) and (1,9)

- Wheel - Two PH3 post holders at coordinates (6,1) and (6,7)
- Rotary encoder - One PH2 post holder at coordinate (5,10)
b. 18 x 12 Optical Board
- Head plate - Two PH3 post holder at coordinates (7,1) and (7,12)
- IR Camera - One PH3 post holder at coordinate (8,9)
- IR LED - One PH6 post holder at coordinate (10,8)
- Handle - Two SH4S038 screws at coordinates (18,4) and (18,10)

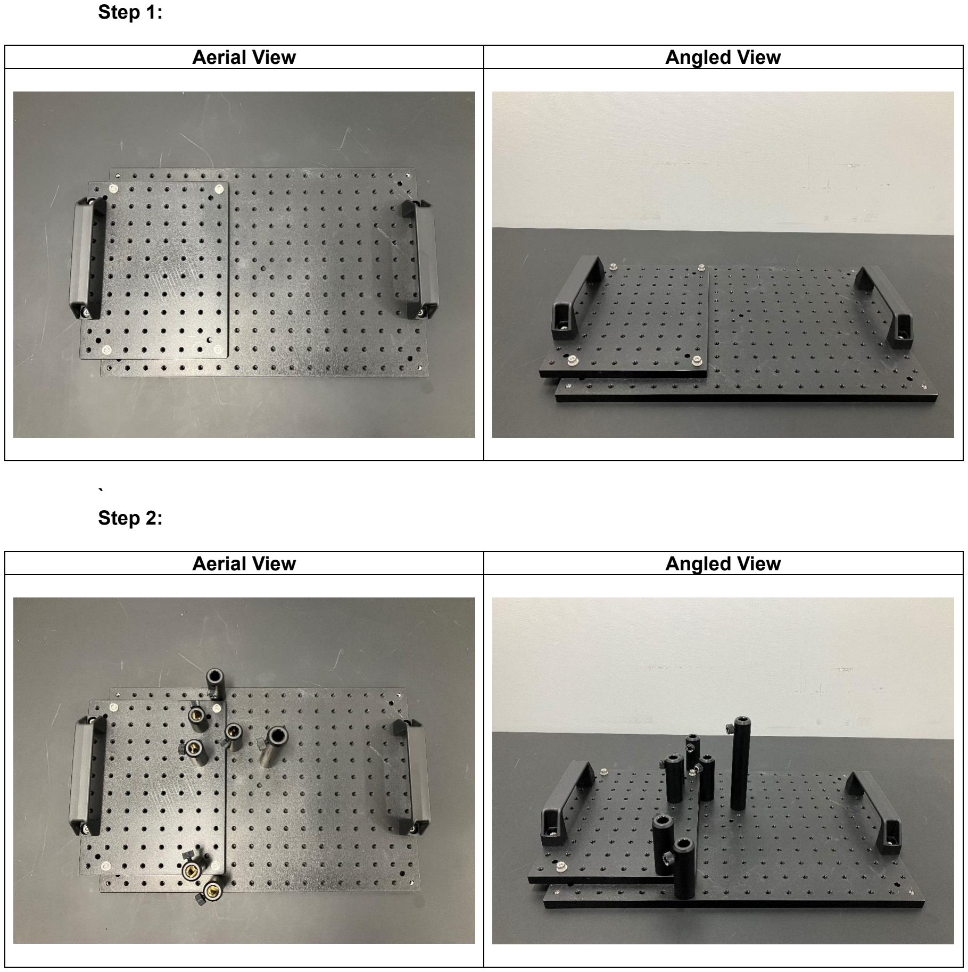
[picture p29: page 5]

Step 1:
Aerial View | Angled View

`
Step 2:
Aerial View | Angled View

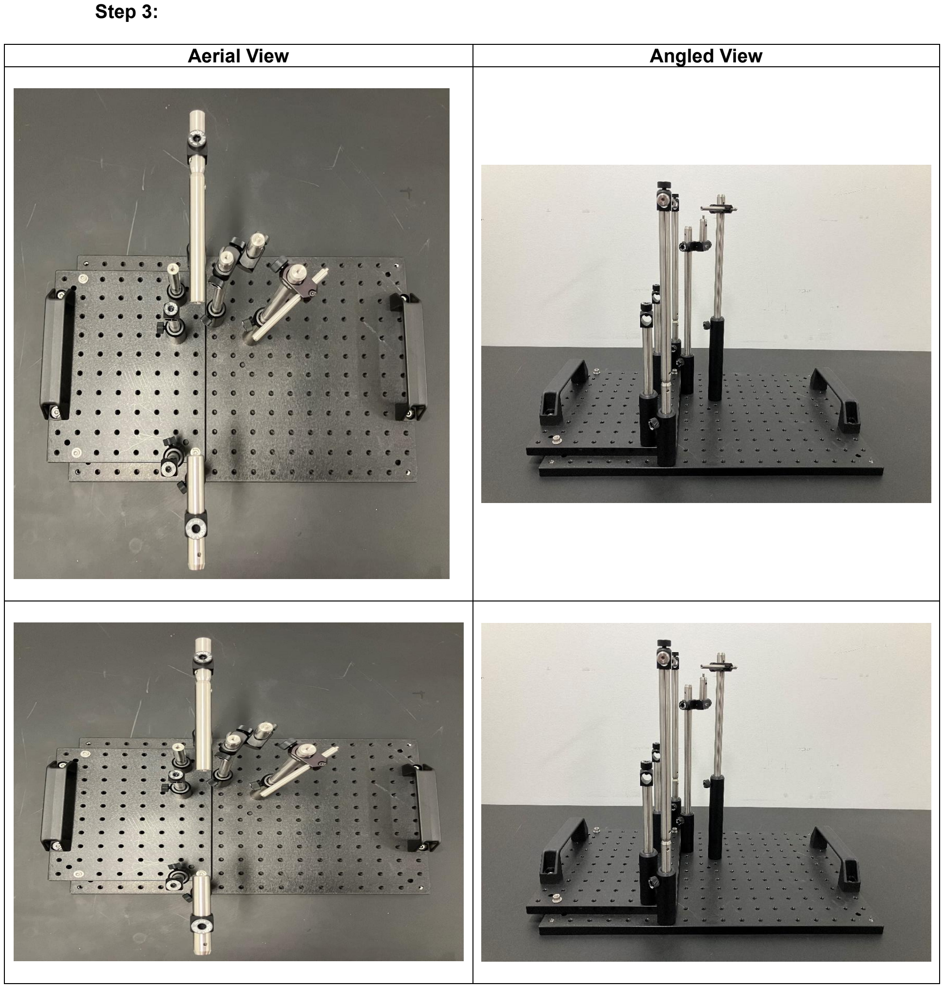
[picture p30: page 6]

Step 3:
Aerial View | Angled View

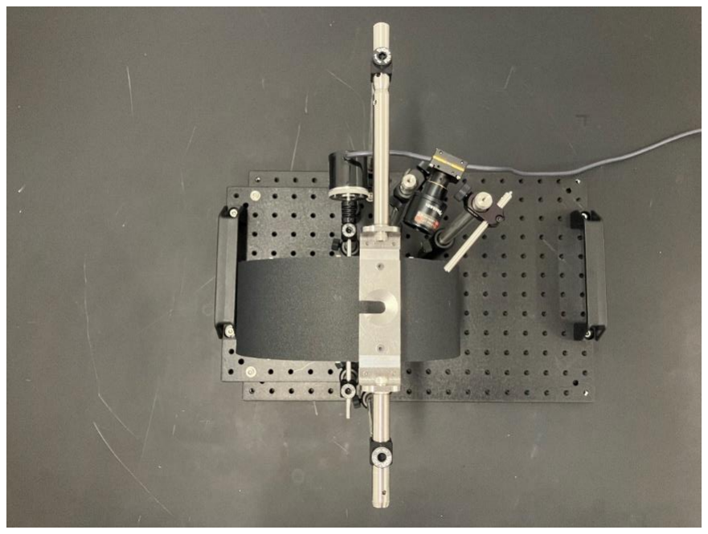
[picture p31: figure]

Step 4:

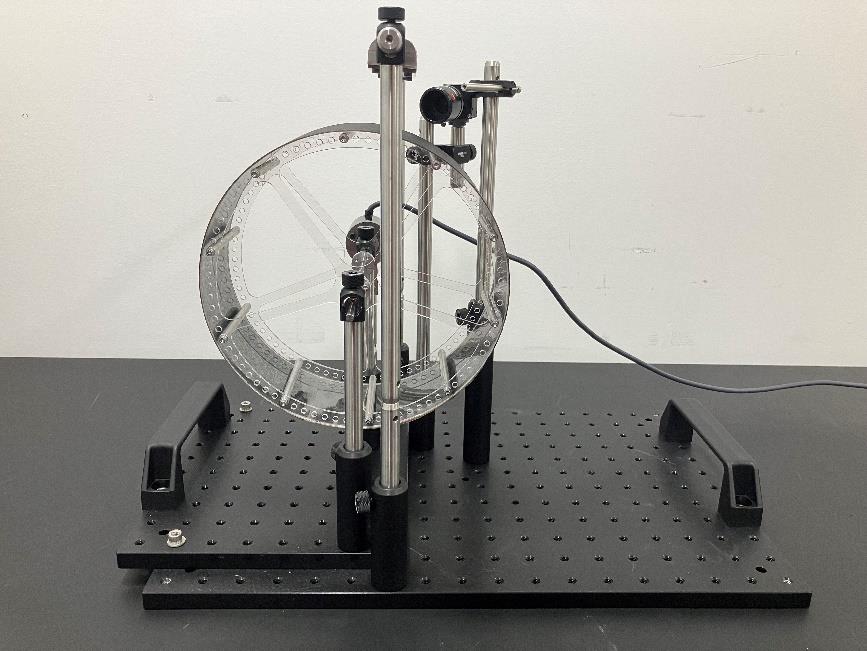
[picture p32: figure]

Aerial View | Angled View

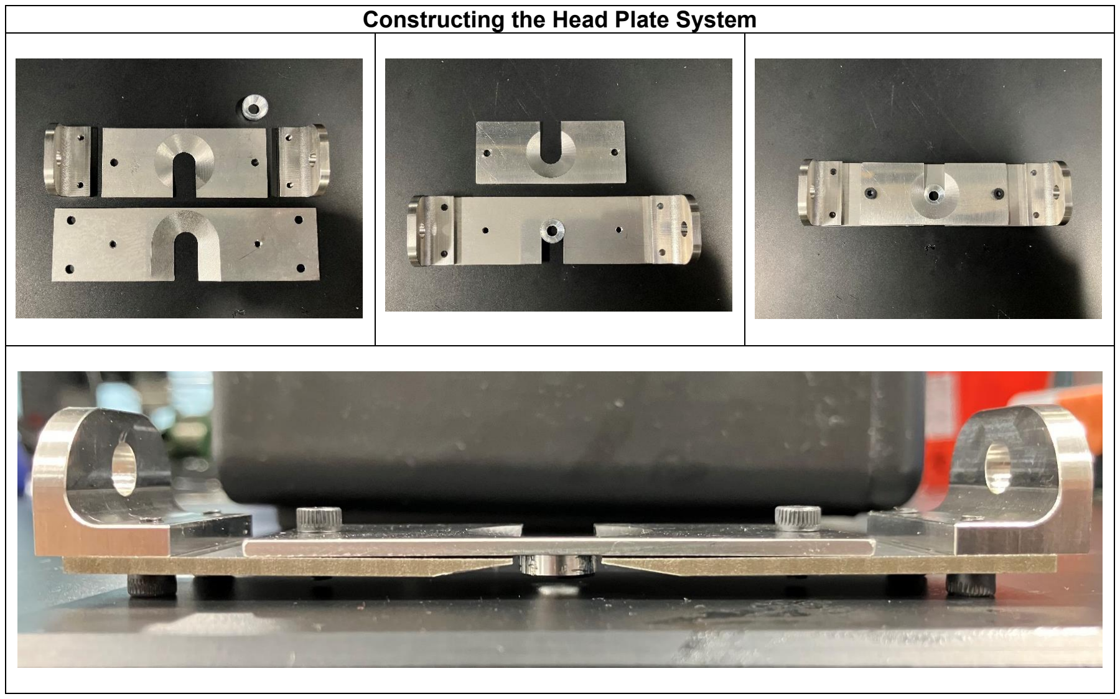
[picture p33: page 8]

Constructing the Head Plate System

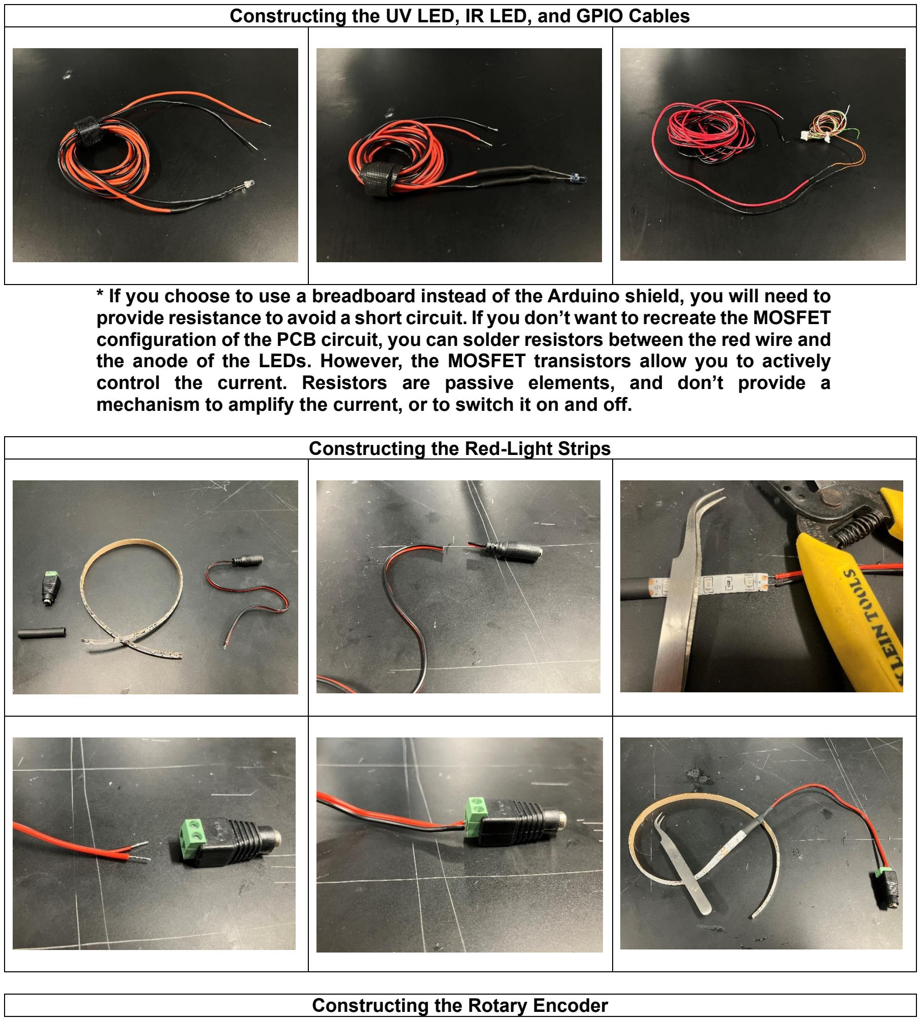
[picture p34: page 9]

Constructing the UV LED, IR LED, and GPIO Cables

* If you choose to use a breadboard instead of the Arduino shield, you will need to provide resistance to avoid a short circuit. If you don’t want to recreate the MOSFET configuration of the PCB circuit, you can solder resistors between the red wire and the anode of the LEDs. However, the MOSFET transistors allow you to actively control the current. Resistors are passive elements, and don’t provide a mechanism to amplify the current, or to switch it on and off.

Constructing the Red-Light Strips

Constructing the Rotary Encoder

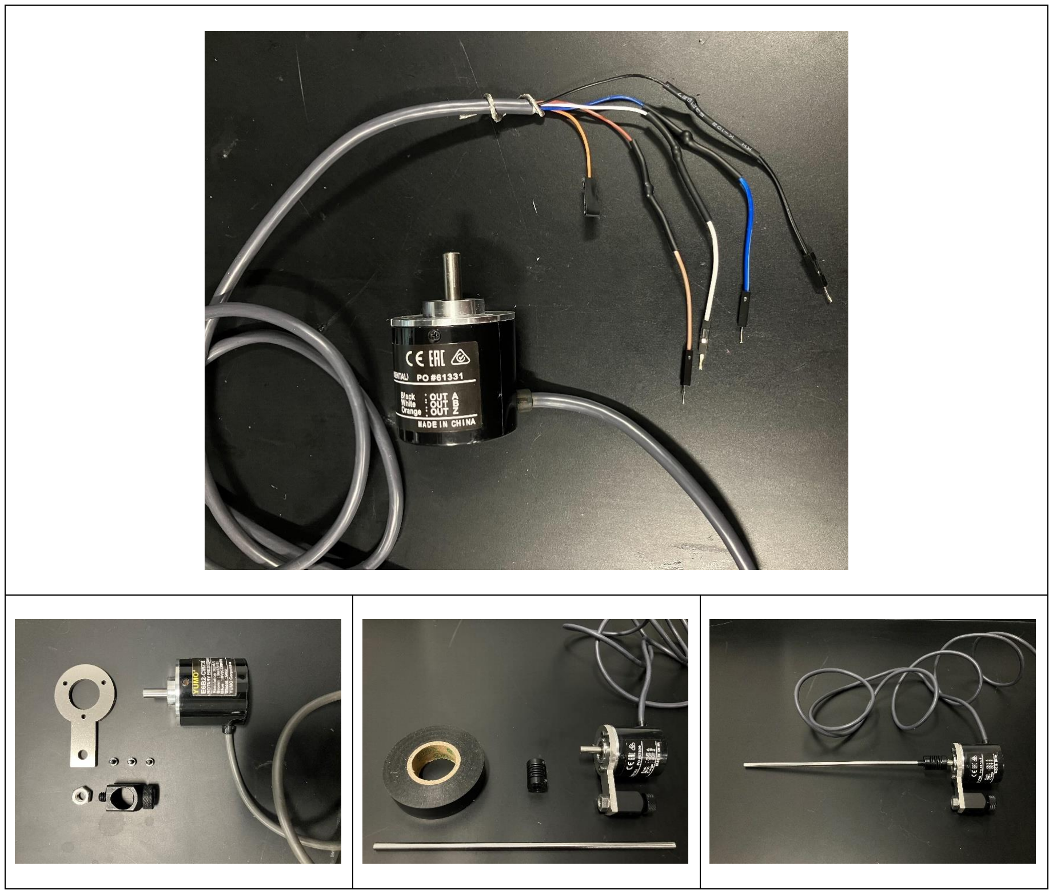
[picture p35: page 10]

Removing the Additional Camera Shutter

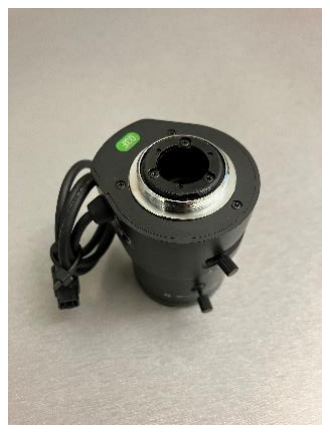
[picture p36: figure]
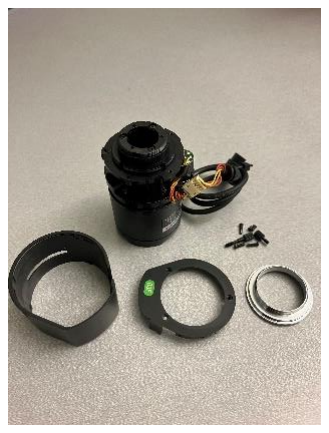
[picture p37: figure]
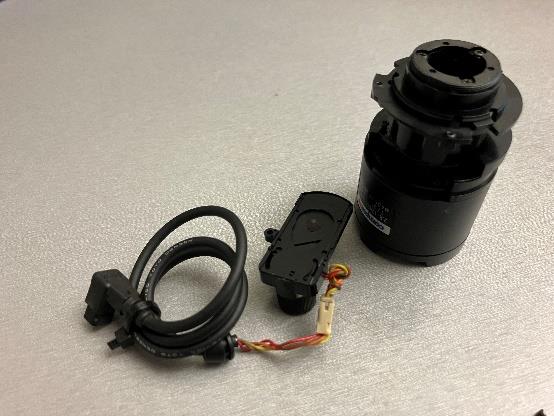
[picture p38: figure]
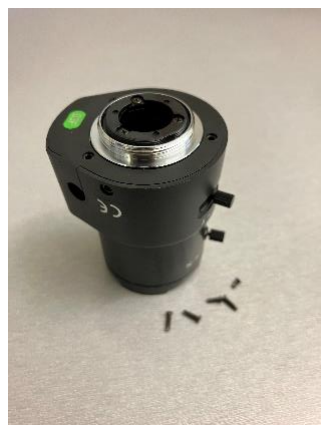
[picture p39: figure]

* Removing the lens shutter of this IR filter lens will allow us to use this lens without an external driver / power supply.

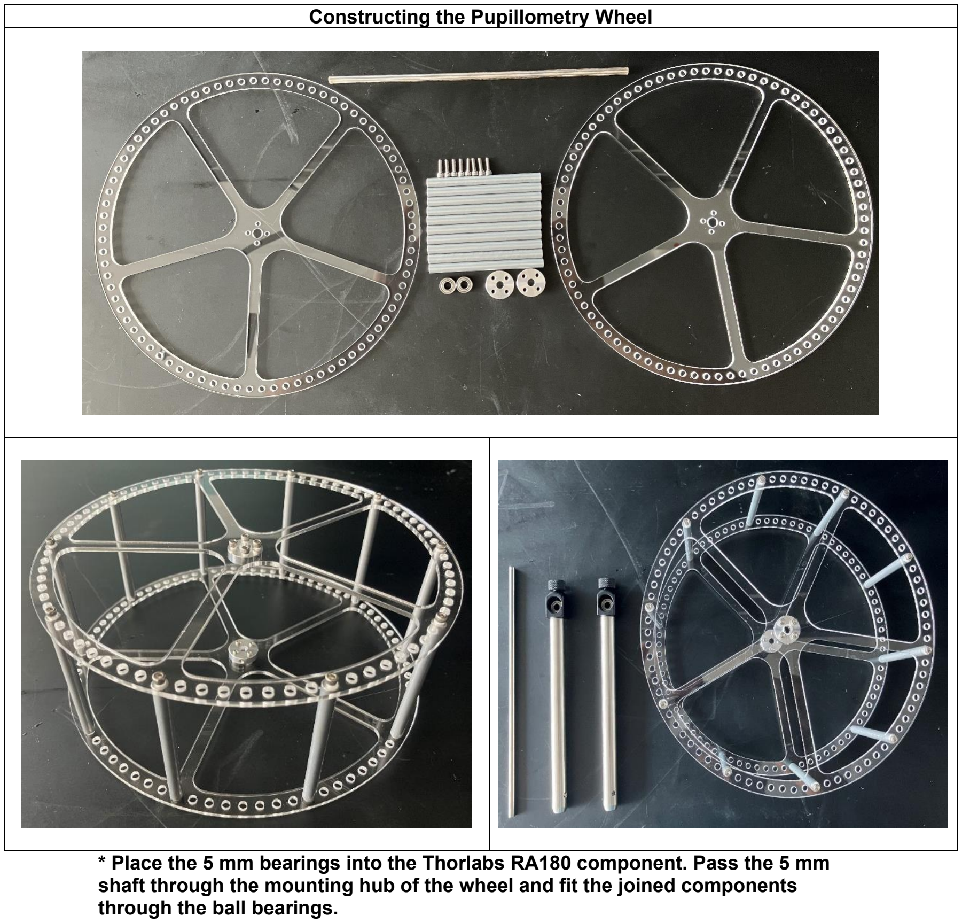
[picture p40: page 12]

Constructing the Pupillometry Wheel

* Place the 5 mm bearings into the Thorlabs RA180 component. Pass the 5 mm shaft through the mounting hub of the wheel and fit the joined components through the ball bearings.

Constructing the Pupillometry Wheel

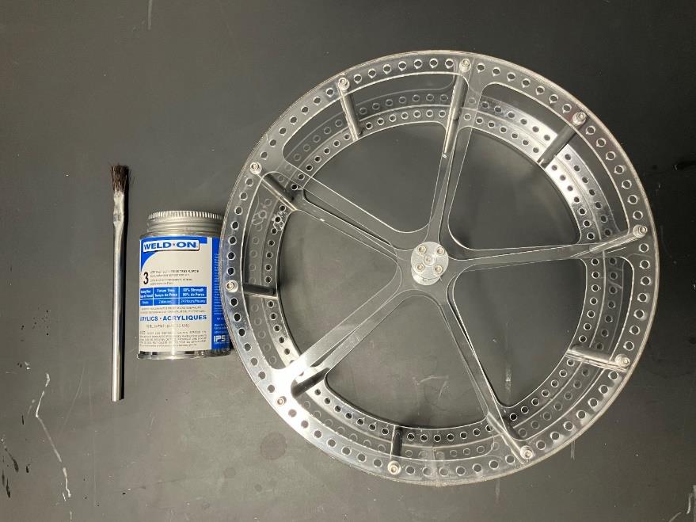
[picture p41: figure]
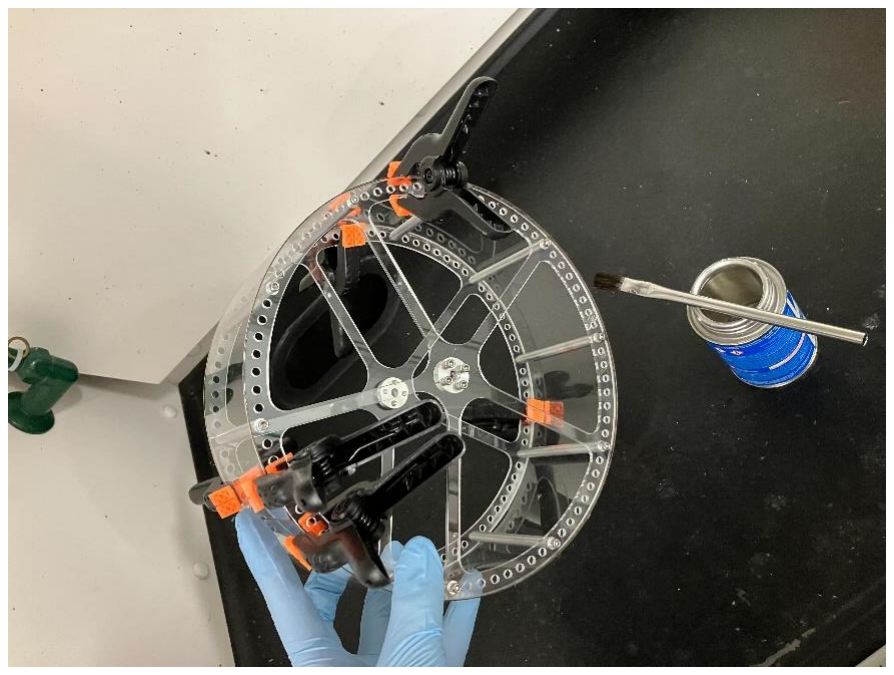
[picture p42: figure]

Installing the Pupillometry Wheel

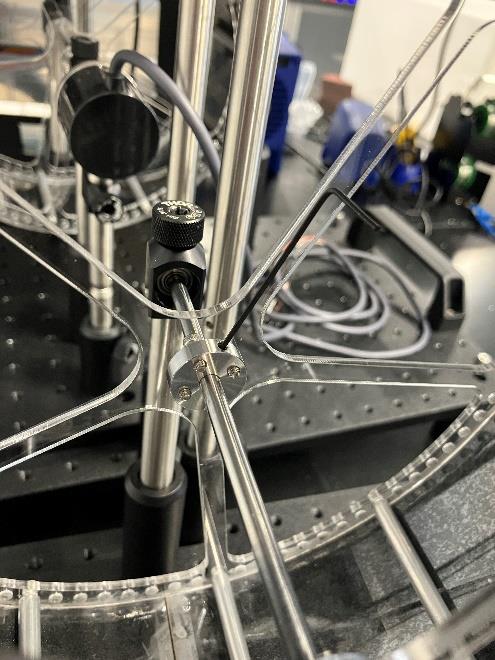
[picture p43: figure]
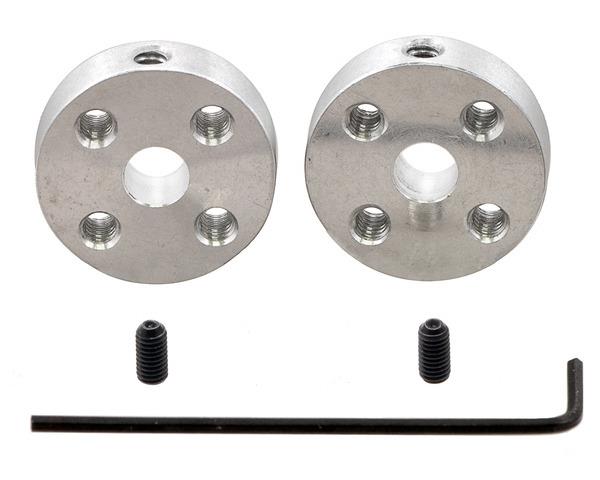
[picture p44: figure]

* The 5 mm mounting hub comes with two smalls screws which can be used to secure the entire pupillometry wheel to the shaft. Tightening this component ensures that movement from the wheel is accurately reflected by the rotary encoder. Insert these two screws into the mounting hub before installing the wheel into the pupillometry system to avoid difficulties.

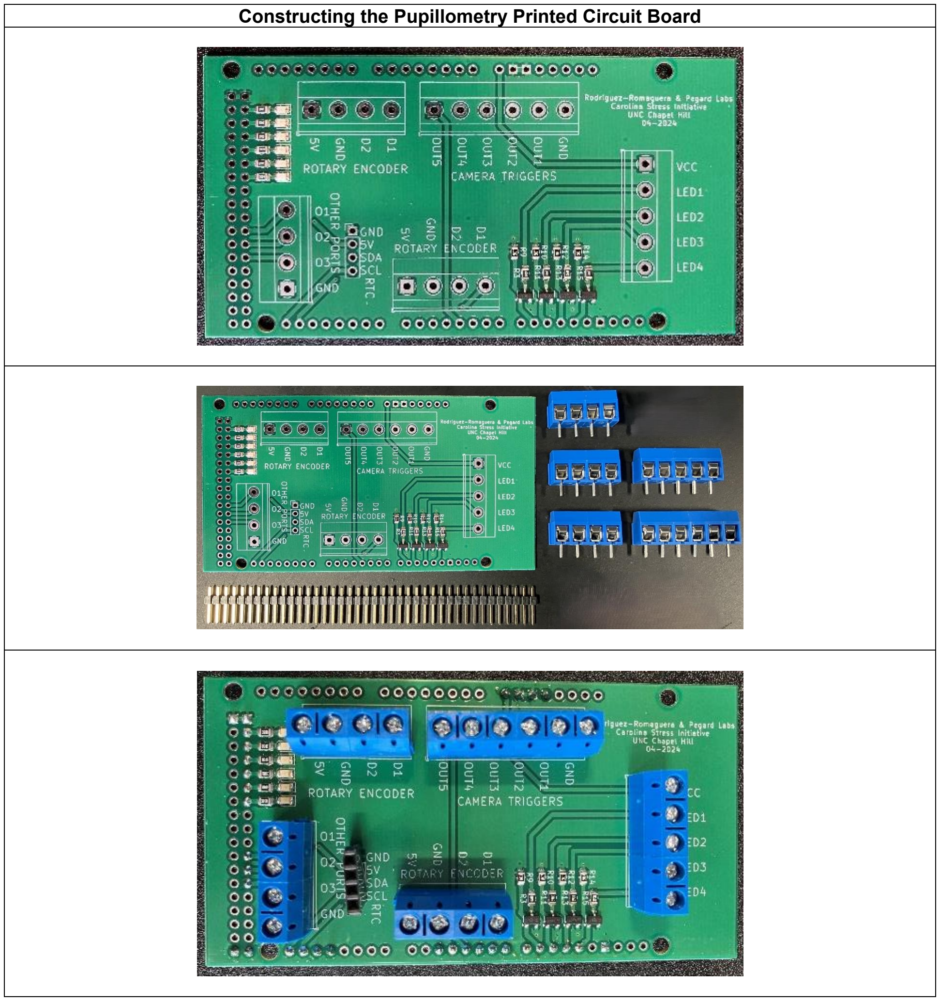
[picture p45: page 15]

Constructing the Pupillometry Printed Circuit Board

### Arduino Compatible Pupillometry Setup PCB

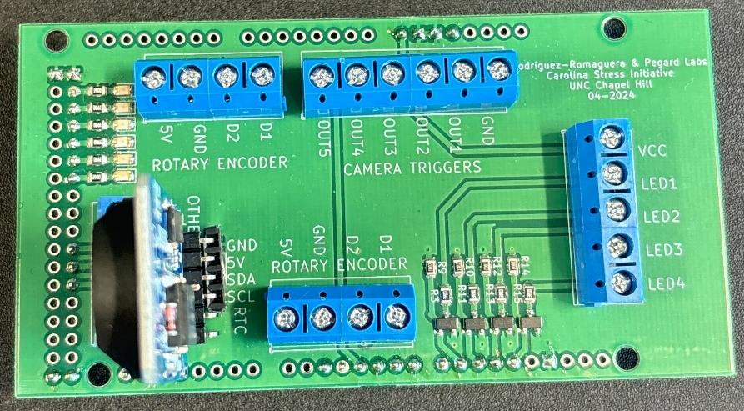
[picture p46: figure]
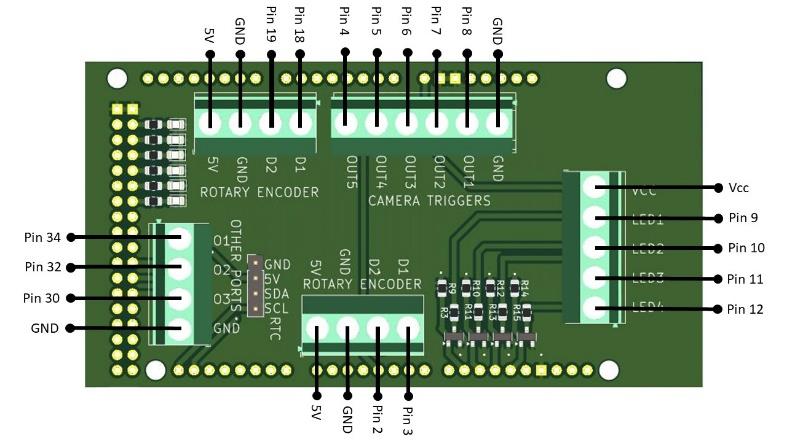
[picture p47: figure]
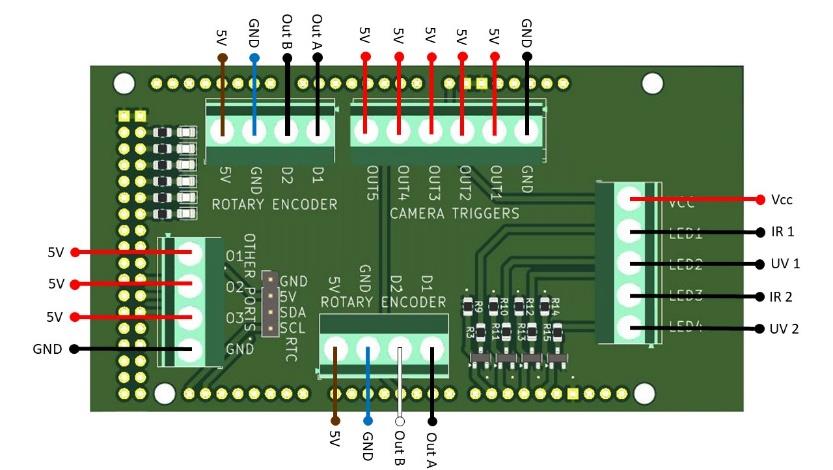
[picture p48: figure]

* The Arduino compatible PCB shield was specifically designed for the purpose of interfacing with all the components necessary for head-fixed experiments. These are the capabilities of the board, based on its current configuration:

UV / IR LED Terminal Block (1 x 5 Terminal at Arduino Pins 9 through 12)
- Four 5 Volt ports in for two UV LEDs and two IR LEDs (With 4 accompanying transistors and resistors)
- One GND port for all four LEDs

Camera/DAQ/Opto Terminal Block (1 x 6 Terminal at Arduino Pins 4 through 7)
- Four trigger ports for two FLIR cameras and two monochrome cameras
- One port for the DAQ and Optogenetic Interference Module
- One GND port for all four cameras, the DAQ, and the Optogenetic interference system

Real Time Clock Terminal Block (1 x 4 Terminal at Arduino Pins D20 SDA and D21 SLA)
- Two input ports for the single RTC
- One PWR for the single RTC
- One GND port for the single RTC

Rotary Encoder #1 Terminal Block (1 x 4 Terminal at Arduino Pins 2 and 3)
- Two output ports for the single rotary encoder
- One PWR for the single rotary encoder
- One GND port for the single rotary encoder

Rotary Encoder #2 Terminal Block (1 x 4 Terminal at Arduino Pins 18 and 19)
- Two output ports for the single rotary encoder
- One PWR port for the single rotary encoder
- One GND port for the single rotary encoder

Other Digital Pins (1 x 4 Termina Block at Arduino Pins 30, 32, and 34)
- Four digital output pins that can be assigned to any additional electrical systems

Fail safe LEDs (6 LEDs at Arduino Pins 42 through 52)
- Six digital output pins that can be assigned to based on relevant binary events
- Two LEDs can be assigned when an input signal is sent to the IR LED
- Two LEDs can be assigned when an output signal has been received from the Rotary Encodes.
- The remaining LEDs can be assigned to indicate a closed loop for any of the cameras or other systems.

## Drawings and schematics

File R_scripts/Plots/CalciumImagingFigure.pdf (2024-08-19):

## Sample_M1_locomotion

## Sample_M1_locomotion

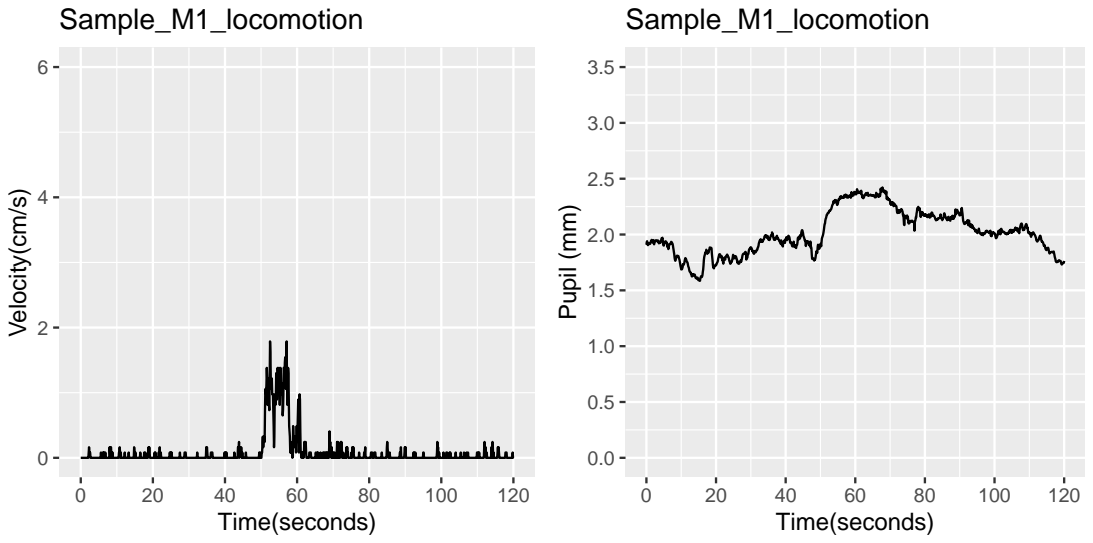
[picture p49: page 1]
Time(seconds); Velocity(cm/s); Pupil (mm)

0

20

40

60

80

20 | 40 | 60 | 80 | 100 | 120

### time(s)

### Neuron

0

8

### value

n=78

## Neural_heatmap_2P_example_data

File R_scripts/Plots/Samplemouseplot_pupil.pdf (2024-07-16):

## Pupil before conversion

## Pupil converted to mm

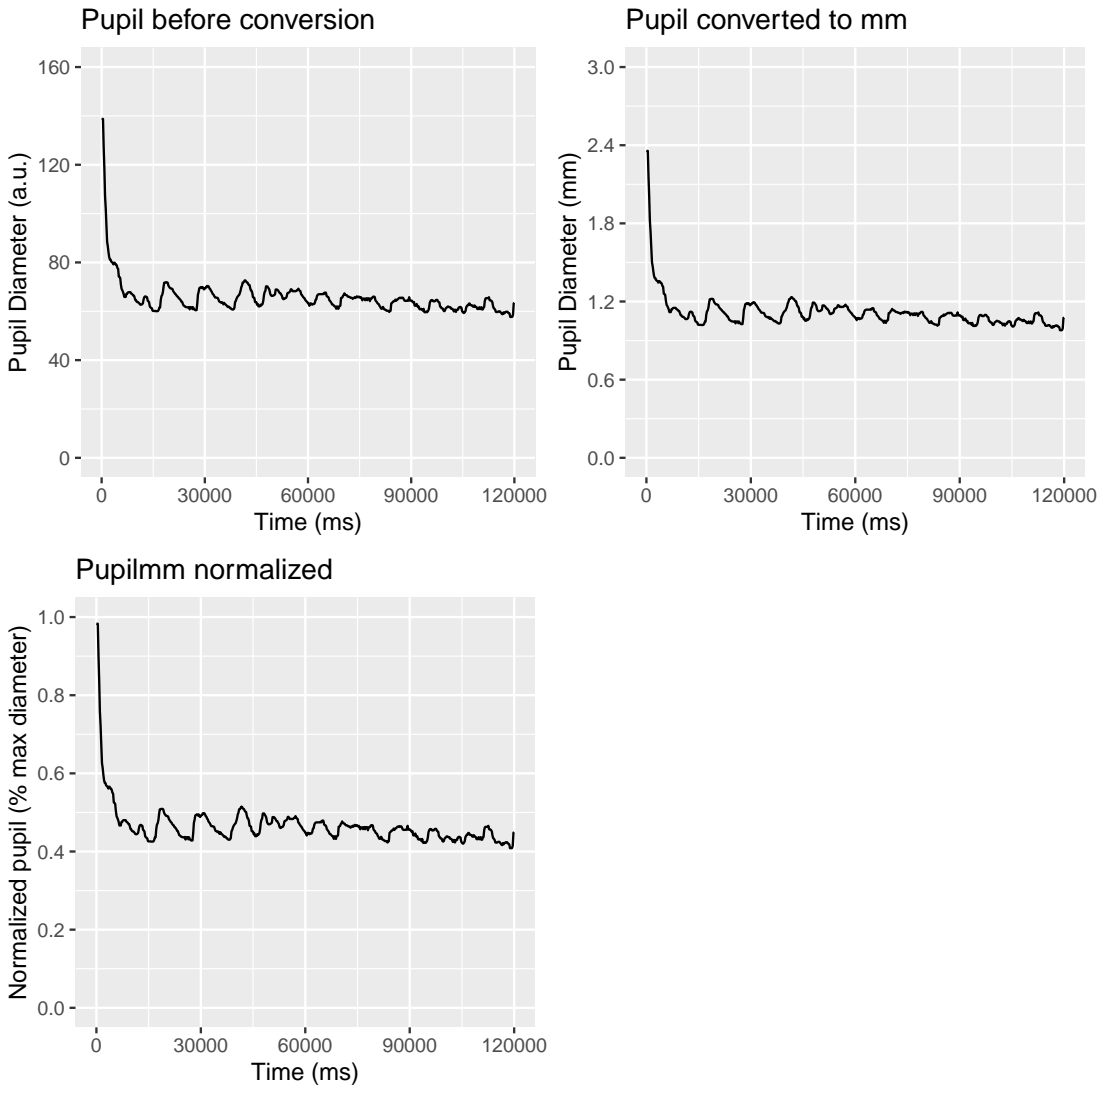
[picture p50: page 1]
Time (ms); Pupil Diameter (a.u.); Pupilmm normalized

Pupil Diameter (mm)

Normalized pupil (% max diameter)

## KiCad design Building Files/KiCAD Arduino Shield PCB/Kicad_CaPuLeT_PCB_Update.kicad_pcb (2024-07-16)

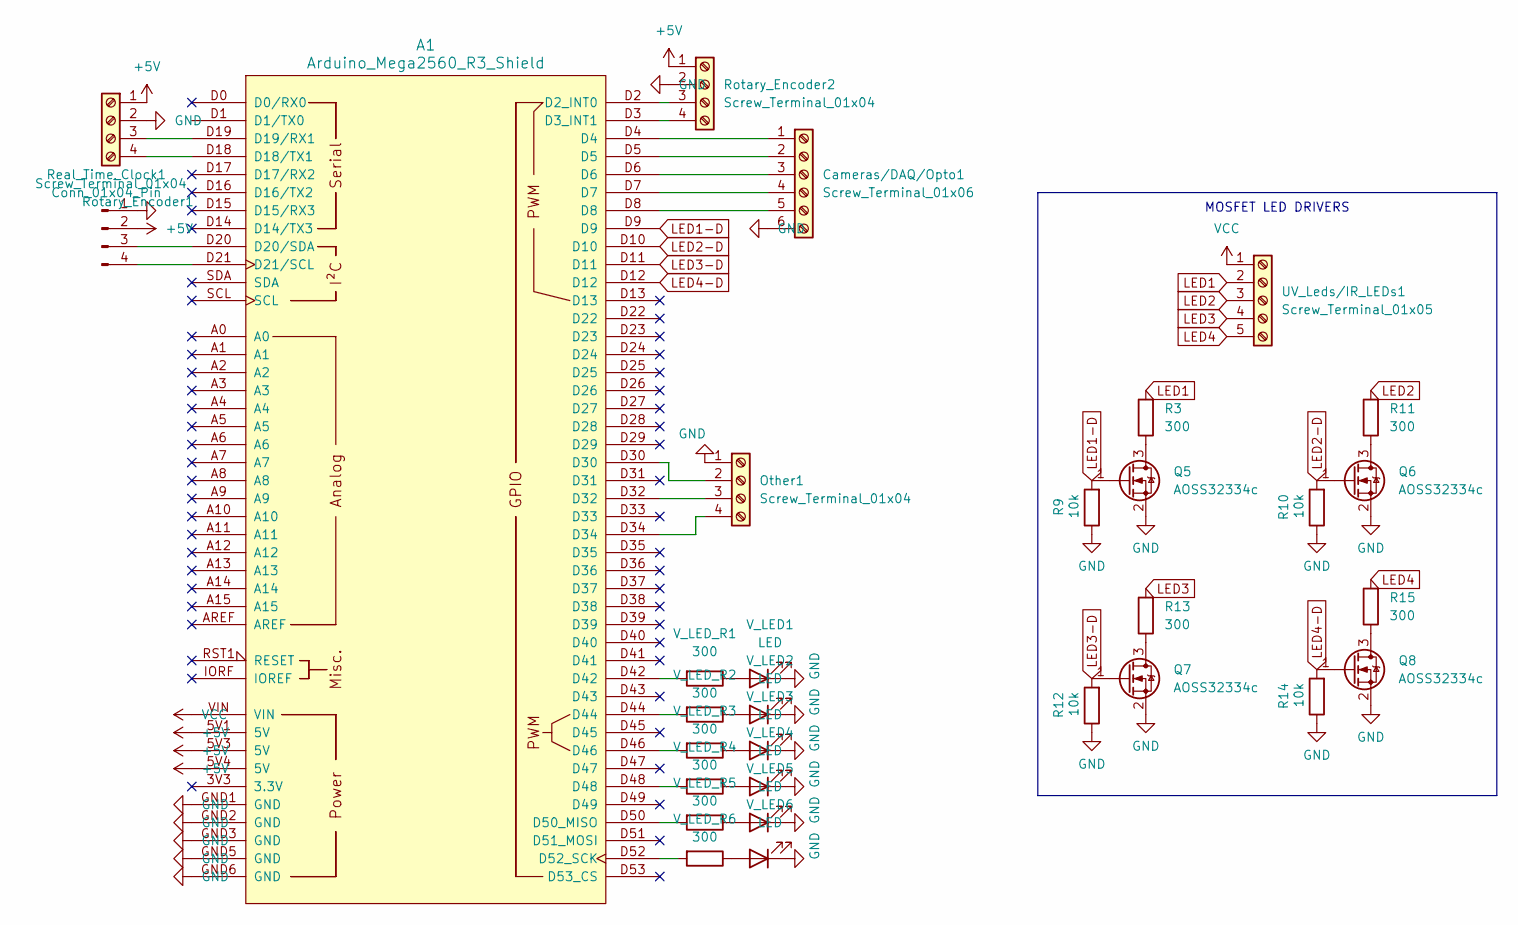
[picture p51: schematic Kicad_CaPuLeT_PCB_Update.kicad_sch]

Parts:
A1: Arduino_Mega2560_R3_Shield; Arduino_Mega2560_R3_Shield_Reduced_Hole
Cameras/DAQ/Opto1: Screw_Terminal_01x06; TerminalBlock_Phoenix_MKDS-1,5-6_1x06_P5.00mm_Horizontal
Other1: Screw_Terminal_01x04; TerminalBlock_Phoenix_MKDS-1,5-4_1x04_P5.00mm_Horizontal
Q5, Q6, Q7, Q8: AOSS32334c; SOT-23
R3, R11, R13, R15: 300; R_0805_2012Metric
R9, R10, R12, R14: 10k; R_0805_2012Metric
Real_Time_Clock1: Conn_01x04_Pin; PinHeader_1x04_P2.54mm_Vertical
Rotary_Encoder1, Rotary_Encoder2: Screw_Terminal_01x04; TerminalBlock_Phoenix_MKDS-1,5-4_1x04_P5.00mm_Horizontal
UV_Leds/IR_LEDs1: Screw_Terminal_01x05; TerminalBlock_Phoenix_MKDS-1,5-5_1x05_P5.00mm_Horizontal
V_LED1, V_LED2, V_LED3, V_LED4, V_LED5, V_LED6: LED; LED_0805_2012Metric
V_LED_R1, V_LED_R2, V_LED_R3, V_LED_R4, V_LED_R5, V_LED_R6: 300; R_0805_2012Metric

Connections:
+5V: A1.5V1 (5V), A1.5V3 (5V), A1.5V4 (5V), Real_Time_Clock1.2, Rotary_Encoder1.1, Rotary_Encoder2.1
GND: A1.GND1 (GND), A1.GND2 (GND), A1.GND3 (GND), A1.GND5 (GND), A1.GND6 (GND), Cameras/DAQ/Opto1.6, Other1.1, Q5.2 (S), Q6.2 (S), Q7.2 (S), Q8.2 (S), R9.1, R10.1, R12.1, R14.1, Real_Time_Clock1.1, Rotary_Encoder1.2, Rotary_Encoder2.2, V_LED1.1 (K), V_LED2.1 (K), V_LED3.1 (K), V_LED4.1 (K), V_LED5.1 (K), V_LED6.1 (K)
LED1: R3.2, UV_Leds/IR_LEDs1.2
LED1-D: A1.D9, Q5.1 (G), R9.2
LED2: R11.2, UV_Leds/IR_LEDs1.3
LED2-D: A1.D10, Q6.1 (G), R10.2
LED3: R13.2, UV_Leds/IR_LEDs1.4
LED3-D: A1.D11, Q7.1 (G), R12.2
LED4: R15.2, UV_Leds/IR_LEDs1.5
LED4-D: A1.D12, Q8.1 (G), R14.2
unnamed: A1.D2 (D2_INT0), Rotary_Encoder2.3
unnamed: A1.D3 (D3_INT1), Rotary_Encoder2.4
unnamed: A1.D18 (D18/TX1), Rotary_Encoder1.4
unnamed: A1.D19 (D19/RX1), Rotary_Encoder1.3
unnamed: A1.D20 (D20/SDA), Real_Time_Clock1.3
unnamed: A1.D21 (D21/SCL), Real_Time_Clock1.4
unnamed: A1.D50 (D50_MISO), V_LED_R5.2
unnamed: A1.D52 (D52_SCK), V_LED_R6.2
unnamed: A1.D42, V_LED_R1.2
unnamed: A1.D44, V_LED_R2.2
unnamed: A1.D46, V_LED_R3.2
unnamed: A1.D48, V_LED_R4.2
unnamed: A1.D4, Cameras/DAQ/Opto1.1
unnamed: A1.D5, Cameras/DAQ/Opto1.2
unnamed: A1.D6, Cameras/DAQ/Opto1.3
unnamed: A1.D7, Cameras/DAQ/Opto1.4
unnamed: A1.D8, Cameras/DAQ/Opto1.5
unnamed: A1.D30, Other1.2
unnamed: A1.D32, Other1.3
unnamed: A1.D34, Other1.4
unnamed: Q5.3 (D), R3.1
unnamed: Q6.3 (D), R11.1
unnamed: Q7.3 (D), R13.1
unnamed: Q8.3 (D), R15.1
unnamed: V_LED1.2 (A), V_LED_R1.1
unnamed: V_LED2.2 (A), V_LED_R2.1
unnamed: V_LED3.2 (A), V_LED_R3.1
unnamed: V_LED4.2 (A), V_LED_R4.1
unnamed: V_LED5.2 (A), V_LED_R5.1
unnamed: V_LED6.2 (A), V_LED_R6.1
VCC: A1.VIN, UV_Leds/IR_LEDs1.1

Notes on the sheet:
MOSFET LED DRIVERS

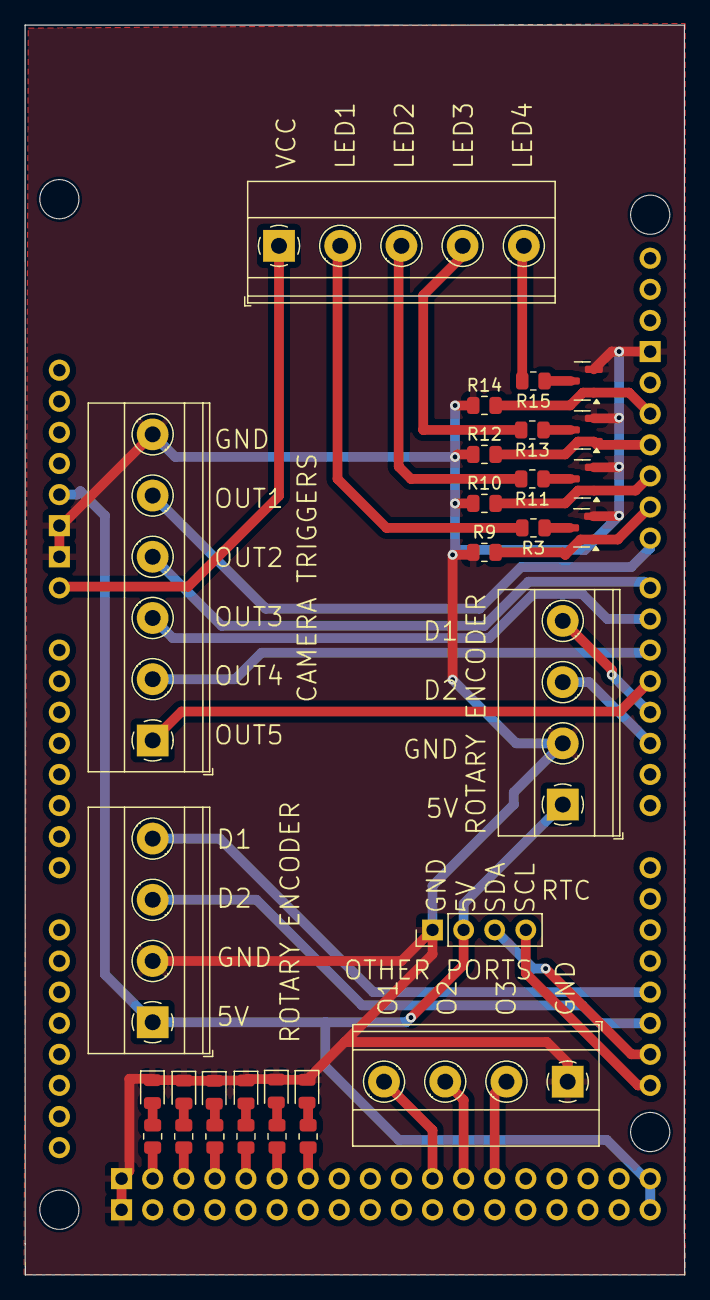
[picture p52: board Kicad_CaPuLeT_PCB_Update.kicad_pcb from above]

Board: 2 copper layers, 53.9 x 102.1 mm, 31 parts (0 on the bottom side), 41 nets.

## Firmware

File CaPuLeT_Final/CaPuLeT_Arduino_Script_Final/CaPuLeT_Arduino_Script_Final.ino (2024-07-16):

/* 
Head-fixed pupillometry and locomotion tracking.

Handles hardware for control of behavioral session for two head-fixation systems.
Use with CaPuLeT GUI.

Parameters for session are received via serial connection from CaPuLeT. Data from hardware is then 
routed directly back via serial connection to CaPuLeT for pupil recordings and output of wheel movement
that is captured from rotary encoders. Hardware system also incorporates a real-time clock (RTC) to correct for 
any drift in output data. 

Serial output is coded as [timestamp from RTC, timestamp from millis, rotary encoder data (steps, signed)]

Serial input is a ten number string. Numbers 1-2 will set Pulse Width Modulation (PWM) for LED, Numbers 3-4 will trigger cameras, 
Number 5 will set sampling speed of rotary encoder, and Number 6 will manually reset RTC. Number 7, 8, and 9 are extra pins that can be configured by the user. 

Input ranges:
"0-255,0-255,0-1,0-1,0-1024,0/1,0/1,0/1,0/1"

example input to reset RTC clock:
"0,0,0,0,50,1,0,0,0" 

*/ 


#include <Wire.h>
#include <DS3231.h>
RTClib RTC;
const int LEDPin[6] = { 42, 44, 46, 48, 50, 52 }; // Define LED pins to indicate system is working properly
const int CameraPin[2] = { 8, 7 }; // Pins to trigger on cameras
const int UVIRLEDPin[2] = { 9, 10 }; // UV and IR LEDs for pupil recording
const int ExtraPin[3] = { 30, 32, 34 }; // Extra pins that can be configured for other functions, 30 is 2P, 11 is for audio, 34 is extra
const int pin_track_a = 18; // Wheel pins which are placed to interrupt
const int pin_track_b = 19;
volatile int track_change = 0;  // Rotations within tracking epochs for wheel 1
signed long track_period = 50;   // Sampling speed of data output  
signed long ts_next_track = track_period;
signed long begintime = 0;
unsigned long startTime = 0; // Variable to store the reference time


void setup() {
  Serial.begin(57600);
  Wire.begin();
  for (int i = 0; i < 6; i++) {pinMode(LEDPin[i], OUTPUT);}
  for (int i = 0; i < 3; i++) {pinMode(ExtraPin[i], OUTPUT);}
  for (int i = 0; i < 2; i++) {pinMode(CameraPin[i], OUTPUT);}
  for (int i = 0; i < 2; i++) {pinMode(UVIRLEDPin[i], OUTPUT);}
  attachInterrupt(digitalPinToInterrupt(pin_track_a), TrackMovement, RISING);
  delay(10);
  DateTime now = RTC.now();
  begintime = now.unixtime();
}

void loop() {
  unsigned long mstime = millis()-startTime;  // Record start of session
  DateTime now = RTC.now();
  unsigned long time = now.unixtime()-begintime;

  // -- TRACK MOVEMENT -- //
  if (mstime >= ts_next_track) {
    if (abs(track_change) > 0) {
      digitalWrite(LEDPin[0], HIGH);
      Serial.print(time);
      Serial.print(",");
      Serial.print(ts_next_track);
      Serial.print(",");
      Serial.println(track_change);
      track_change = 0;
      digitalWrite(LEDPin[0], LOW);
    }
    ts_next_track = ts_next_track + track_period;     // Increment ts_next_track for next track stamp
  }

  if (Serial.available() > 0) {  //look for serial communication from CaPuLeT 
    digitalWrite(LEDPin[1], HIGH);  // Acknowledgement that serial string was received 
    String serialData = Serial.readStringUntil('\n');
    int values[9];  // 9 ints expected
    int count = 0;
    char *token = strtok(const_cast<char *>(serialData.c_str()), ",");
    while (token != NULL && count < 9) {
      values[count++] = atoi(token);
      token = strtok(NULL, ",");
    }
    for (int i = 2; i < 4; i++) {digitalWrite(CameraPin[i-2], values[i]);}  // update Camera triggers to on state
    for (int i = 0; i < 2; i++) {analogWrite(UVIRLEDPin[i], values[i]);}  // update LEDS
    track_period = values[4]; // update sampling speed

    if (values[5] == 1) {
      DateTime now = RTC.now(); // reset time
      begintime = now.unixtime();
      values[5] == 0;
    }

    if (values[6] == 1){ // update 2P trigger to on state
      digitalWrite(ExtraPin[0], HIGH);
    }
      
    startTime = millis();
    ts_next_track = track_period;
    digitalWrite(LEDPin[1], LOW);                                       // indicate acknowledgment
    for (int i = 2; i < 4; i++) {digitalWrite(CameraPin[i - 2], 0); }  // update Camera triggers to off state
    digitalWrite(ExtraPin[0], LOW); // update 2P trigger to off state 
  }
}

void TrackMovement() {
  // Track changes in rotary encoder via interrupt. If don't have an interrupt, data values are missed
  if (digitalRead(pin_track_b)) track_change++;
  else track_change--;
}

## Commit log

2024-01-05 Update and rename Headring_mod_five_eighths_cut.step to Headring_five_eighths.step
    [Headring_five_eighths.step]
2024-01-05 Update and rename HeadPlateHolderbottomthreaded.step to HeadPlateBottomThreaded.step
    [HeadPlateBottomThreaded.step]
2024-01-05 Update and rename HeadPlateHolderthreaded.step to HeadPlateThreaded.step
    [HeadPlateThreaded.step]
2024-01-08 Rename c) Pupillometry Wheel Cost Spreadsheet.xlsx to 3-Pupillometry-Wheel-Cost-Spreadsheet.xlsx
    [3-Pupillometry-Wheel-Cost-Spreadsheet.xlsx]
2024-07-16 Create KiCAD Arduino Shield PCB
2024-07-16 Add R_scripts used to analyze some data in CaPuLeT Protocol Paper
    [Calciumimagingdata_aggregated.csv, HabSample_Mouse_DLC.csv, HabSample_Mouse_Wheel.csv, corner_pts_Sample_Mouse.csv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]
2024-08-18 Update CalciumImaging_Script.R
    Fixed the overlap in numbers for the x-axis in the neural heatmap figures
2024-08-19 Add files via upload
    Update to Neural Heatmap figure so that x-axis labels do not overlap.
